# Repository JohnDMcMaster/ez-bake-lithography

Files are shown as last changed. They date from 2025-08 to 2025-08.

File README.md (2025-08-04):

# ez-bake-lithography
Low cost silicon lithography machine

Aliexpress "EPROM ERASER" ("ay-fw-ccq" PCB inside):
  * Buy a teal EPROM eraser (ex: https://www.aliexpress.us/item/3256802806741194.html)
    * Should be about $30 delivered
  * Print ay-fw-ccq_carrier_r4.stl

PE-140T version:
  * Buy a Spectroline PE-140T
    * Surplus price varies wildly. However you can get it without the drawer => cheaper unit
    * Remove the bottom cover
    * Bypass the interlock (ex: shim it)
  * Print pe140t_carrier_r1.stl
  * Print wafer-holder_r2.stl

Regardless, for each mask:
  * Print transparency-frame_inner_r1.stl
  * Print transparency-frame_outer_r1.stl
  * I had to run the transparency through my printer twice for it to be reasonably dark
  * Cut out the mask from the transparency

Reference transparency flow
  * Transparency: Uinkit https://www.amazon.com/dp/B078R4DGSB?ref=ppx_yo2ov_dt_b_fed_asin_title&th=1
  * Printer: Brother HL-L2390DW
  * Linux print: settings => no scaling
  * Put transparency in the main paper tray as the only thing in there
    * Its hard to feed from the side feeder with consistent alignment
  * Print => 2 copies
  * Let it print the first pass / copy
  * Without rotating or flipping, feed it into the tray a second time
    * If you do try feeding from the side, you need to flip it over vertically
  * Let it print the second pass / copy
  * Check alignment
    * Usually upper right is best aligned
    * Try again if it doesn't look right
  * General tips
    * It jammed a lot. Its not a fun process
    * Adjusting Windows driver toner darkness (official brother driver) did nothing
    * I don't see a printer menu setting to adjust toner darkness

Reference developing flow
  * Spin on photoresist
    * P4620 photoresist
    * Use Maasi spin coater
    * ~0.8 mL
    * 2" wafer
    * 4200 RPM @ 30 sec
  * Soft bake phototresist
    * 3 minutes @ 125C on hot plate
  * Exposure
    * PE-140T: expose for 15 minutes
  * Develop
    * 200 to 500 mL of 18% w/v KOH solution
      * Aim for 300 mL min
      * Ex for 300 mL
        * 54 g KOH
        * 300 mL DI H2O
      * Smaller amounts of solution lead to inconsistent developing
    * Using carbon fiber tweezers, waft wafer for ~30 seconds
    * Waft in 300 mL DI water (tank 1) until photoresist think clouds are gone (~10 seconds)
    * Waft in 300 mL DI water (tank 2) for final clean
    * Optional: spin and/or blow dry for best result
  * Inspect under microscope
    * If you have done this correctly you should see no photoresist on wafer and still photoresist where the pattern was

More notes here: https://docs.google.com/document/d/17HMt2Zzm5FRwCRLVQvpPXudmmuqpur_HYsEFmfIFAqE/edit?tab=t.0#heading=h.3smdsrxmfbn6

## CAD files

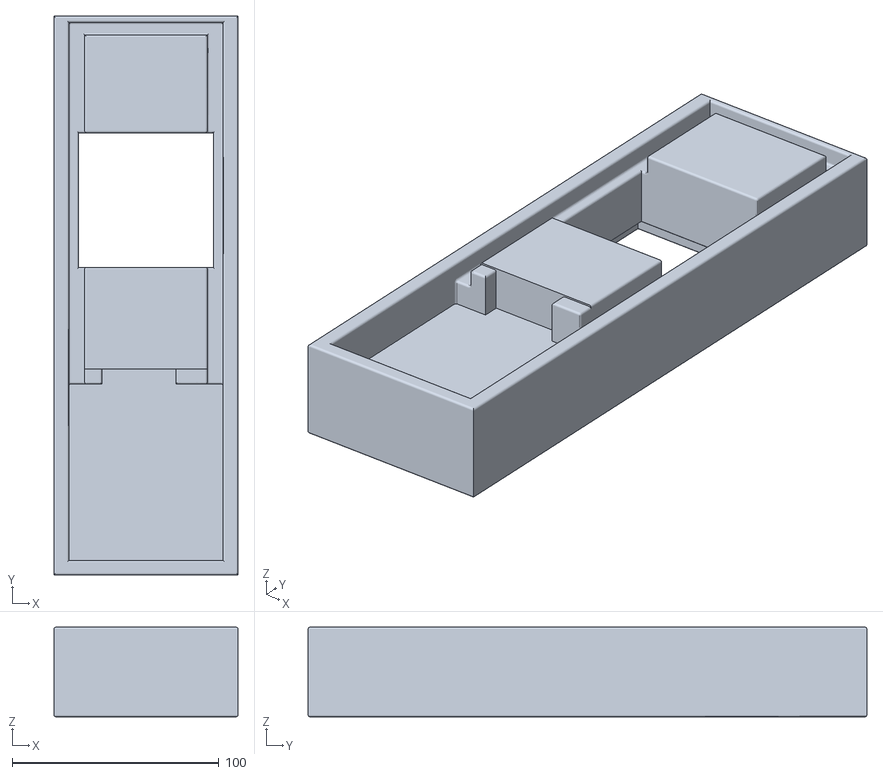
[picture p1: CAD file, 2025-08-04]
machine/pe140t_carrier_r1.stl
88.9 x 270.0 x 43.4

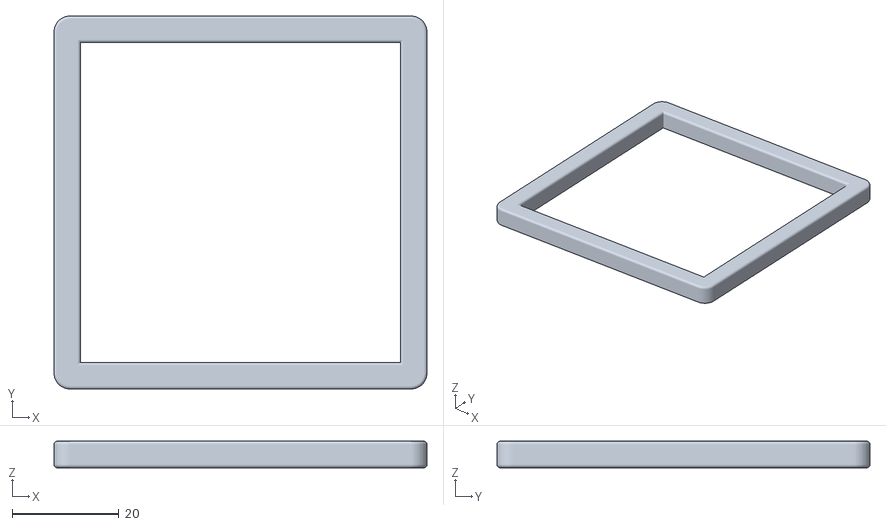
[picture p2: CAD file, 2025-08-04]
machine/transparency-frame_inner_r1.stl
70.0 x 70.0 x 5.00

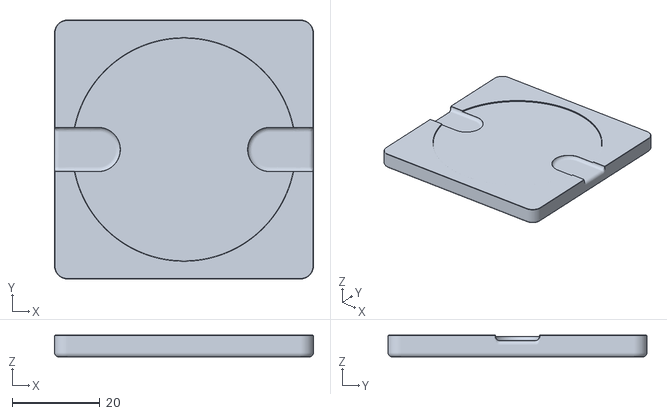
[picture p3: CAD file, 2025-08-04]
machine/wafer-holder_r2.stl
59.2 x 59.2 x 5.00

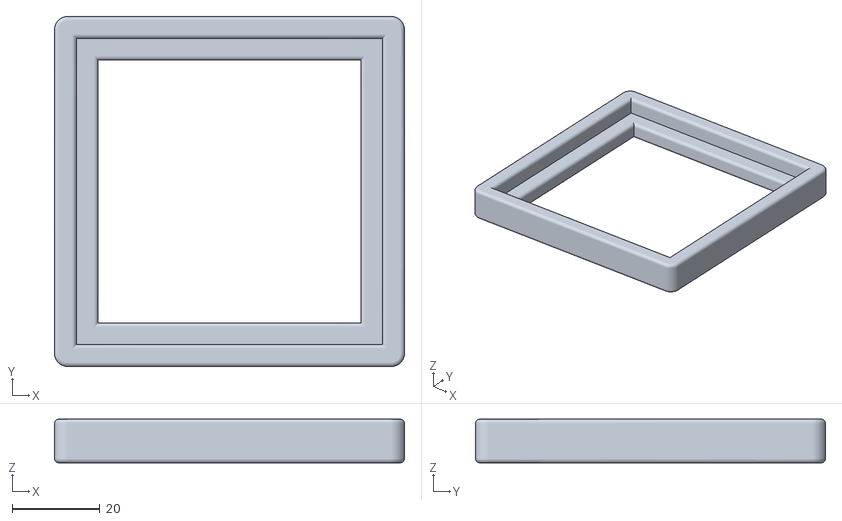
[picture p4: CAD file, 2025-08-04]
machine/transparency-frame_outer_r1.stl
80.0 x 80.0 x 10.0

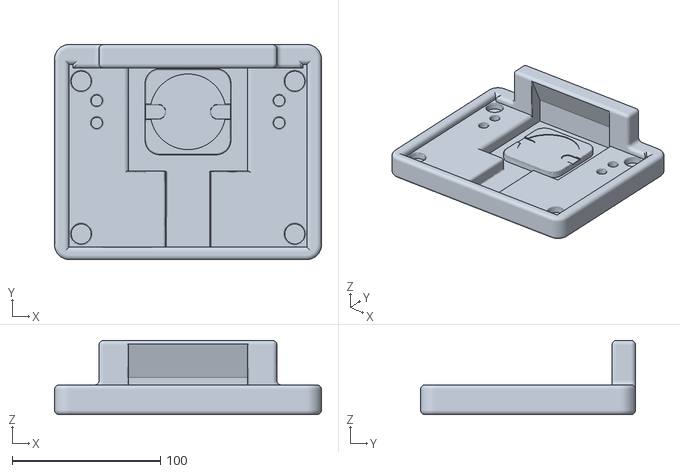
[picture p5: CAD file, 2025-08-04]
machine/ay-fw-ccq_carrier_r4.stl
180.0 x 145.0 x 50.0
